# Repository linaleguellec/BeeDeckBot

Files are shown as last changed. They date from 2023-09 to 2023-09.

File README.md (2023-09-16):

# Project presentation 
I completed this project as part of my final year internship as a general engineer specializing in mechanical engineering. 
The aim of the project is to use a single camera to shoot 3D images of bees landing on a moving robotic flower. For more details on the background to this project, please consult my internship report. 

# Folders organization
- beeTracking  : all the algorithms for post-processing the videos (tracing the bee's 3D trajectory from a video in mp4 format). 
- MotorControl : arduino algorithms for motor control.
- robotCAD : the complete digital model of the steel structure in both SolidWorks and STEP formats. 
- technicalDocumentation : all technical documentation (Dynamixel Servomotors, RFID gate ... ). 
- videos : examples of videos taken with the metal structure. The quality of the videos has been reduced to being stored on GitHub.
- results : a summary video of an example of possible results. The quality of the videos has been reduced to being stored on GitHub. 

# Comments  

"MotorControl", "robotCAD", "technicalDocumentation and videos" folders are ready to use. You can use them directly for your projects.

Folders "beeTracking" is not yet powerful enough to be used directly in your projects. I therefore advise you to use them as a first step in your research. 

# Equipment to purchase 
- [a cart](https://www.manutan.fr/fr/maf/table-roulante-noire-2-plateaux-capacite-150-kg-a688743)
- [an RFID door](https://www.microsensys.de/en/solutions/small-animals-identification/)
- [a camera that films at 500 fps](https://www.back-bone.ca/rx0-mod/)
- Please refer to the "invoice" appendix of my internship report for the metallic structure's equipment.

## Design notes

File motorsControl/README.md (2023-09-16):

# Presentation  
This README explains how to set up the electronics to control the motors. In particular, how to start and stop the robotic flower's motors using the manual switch and the RFID door switch. 

# User guide 
Once the metal structure has been assembled, install all the electronic circuits. Transfer the code in this folder to the Arduino UNO board. First, make sure that the electronic circuit without the RFID door is working. Press the manual switch once, the robotic flower target should move with random frequency and amplitude. Press a second time, and the target should stop and move to the position for the next start. 

## Electronics 
Here's the real and theoretical electronic circuit. I've placed the integrated switch of the RFID port and the manual switch in parallel. In this way, the motors of the robotic flower can be controlled either manually by the manual switch, or automatically by the RFID door switch. 
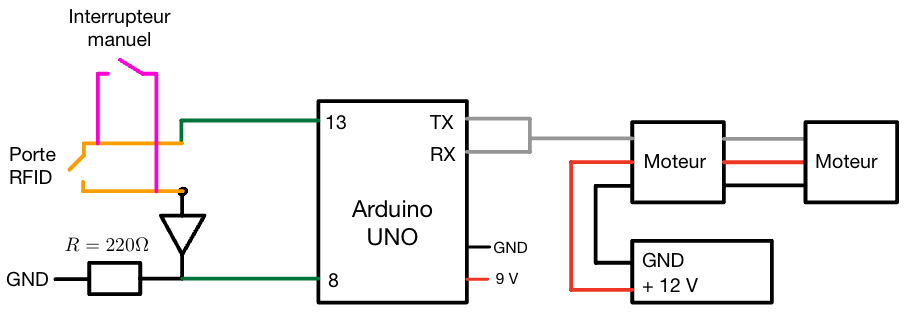
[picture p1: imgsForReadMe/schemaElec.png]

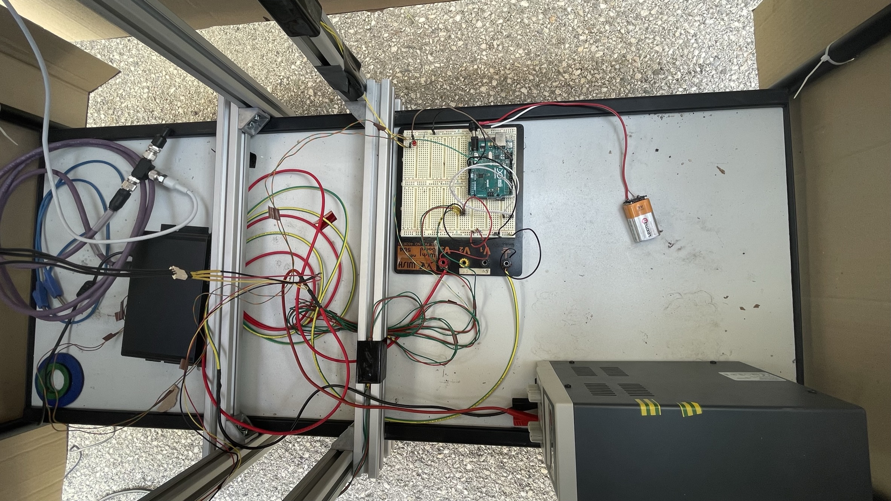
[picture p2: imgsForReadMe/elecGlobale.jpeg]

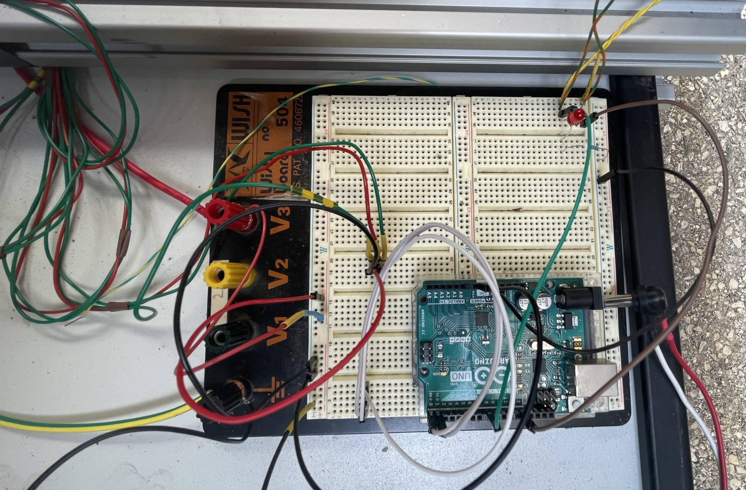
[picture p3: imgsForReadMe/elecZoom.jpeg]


## RFID gate 
- Install the RFID door according to this [technical documentation.](https://github.com/linaleguellec/BeeDeckBot/tree/main/technicalDocumentation/RFIDgate)  

- Attach wires to the back of the RFID door controller as follows. These are the wires for the RFID door's built-in switch. Indeed, as soon as the RFID door detects a bee, the door controller quickly closes its switch. Here's the electronic design from the technical documentation.
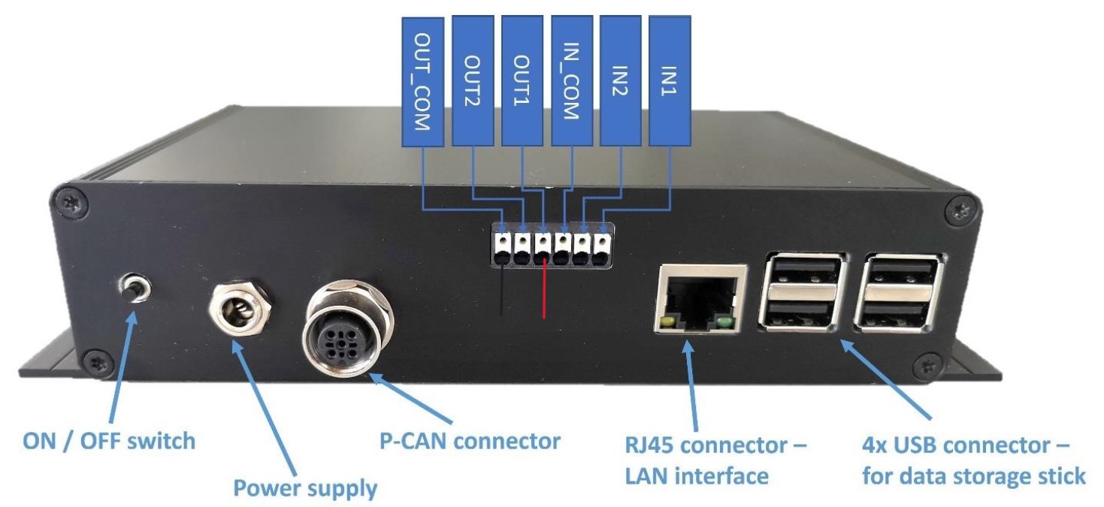
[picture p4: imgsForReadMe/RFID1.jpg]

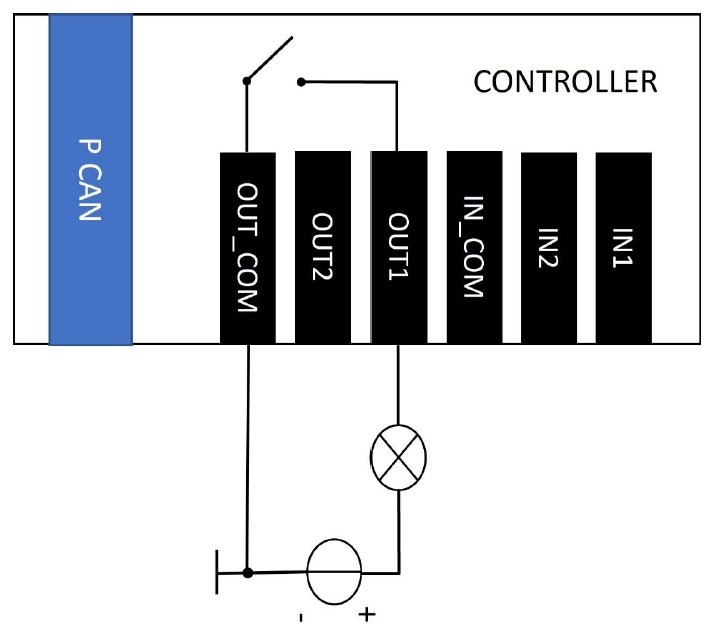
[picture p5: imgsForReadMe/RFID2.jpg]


- For more information about the technical operation of the RFID door, please refer to the ["technical documentation" folder.](https://github.com/linaleguellec/BeeDeckBot/tree/main/technicalDocumentation/RFIDgate)

## Robotic flower control
Please refer to my internship report for an explanation of the robotic flower's motor control algorithm.

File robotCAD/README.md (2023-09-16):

# presentation
In this folder, you'll find all the CAD files for the metallic structure in SolidWorks and Step format. 

# General assembly guide 

- Assemble the flight chamber. 
- Remove the floor from the upper part of the cart.  
- First of all, mount the centre of the metallic part. The part that links the camera, flight chamber, cart and robotic flower.  This part is mounted like a sandwich between the upper rails of the carriage. Adjust its position along the length of the cart so that, once the whole structure is assembled, the 4 wheels of the cart support an equivalent weight. 
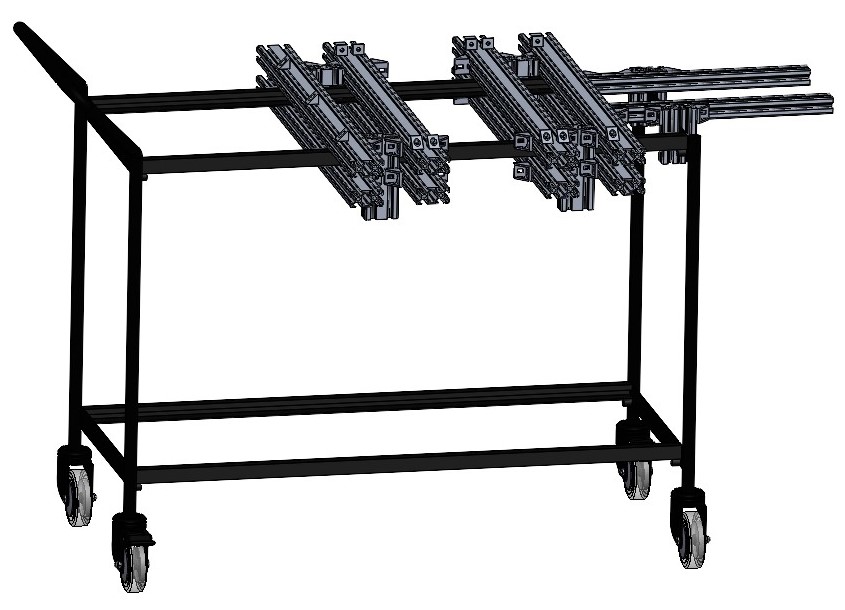
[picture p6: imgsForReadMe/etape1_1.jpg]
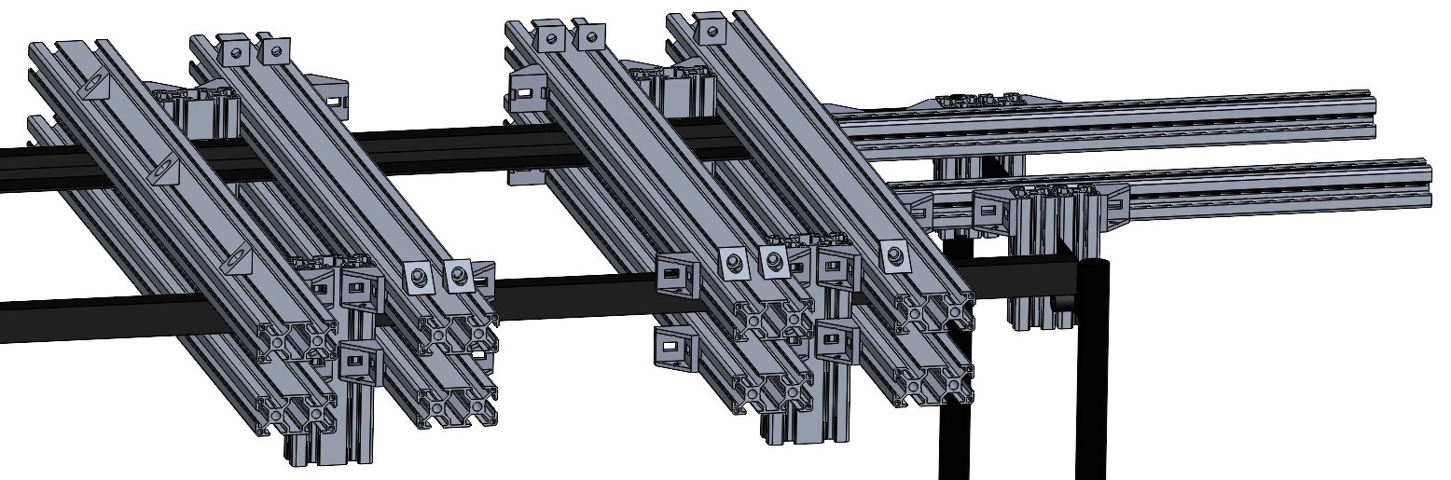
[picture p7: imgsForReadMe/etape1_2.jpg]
 
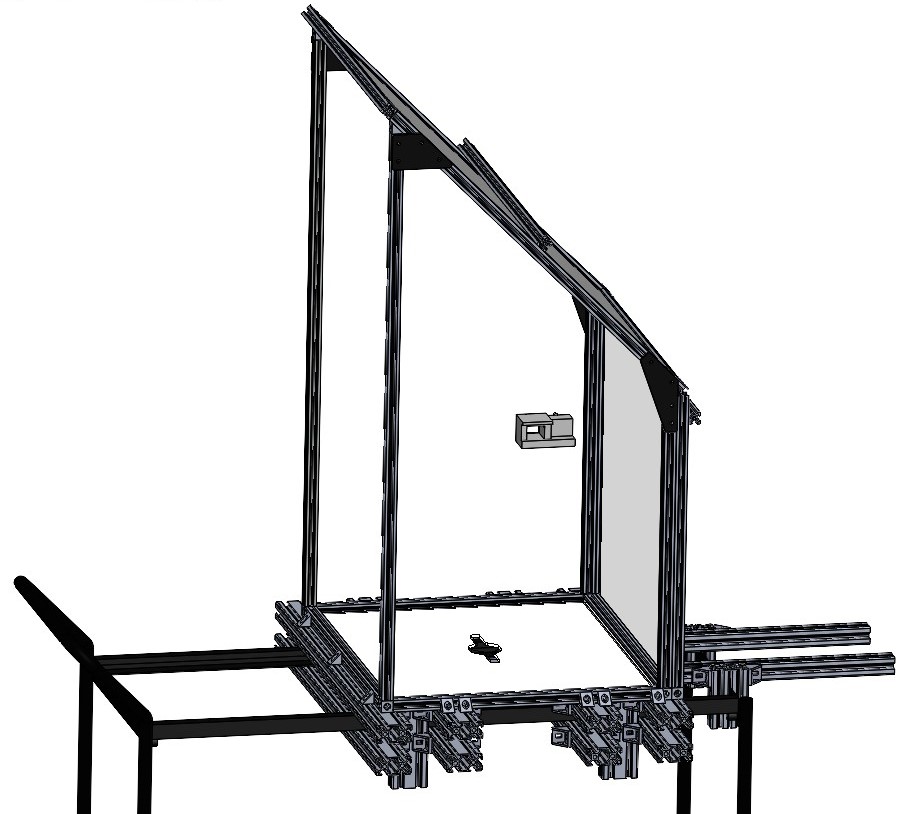
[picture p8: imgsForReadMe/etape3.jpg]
- Attach the flight chamber to the centre of the metal part. 
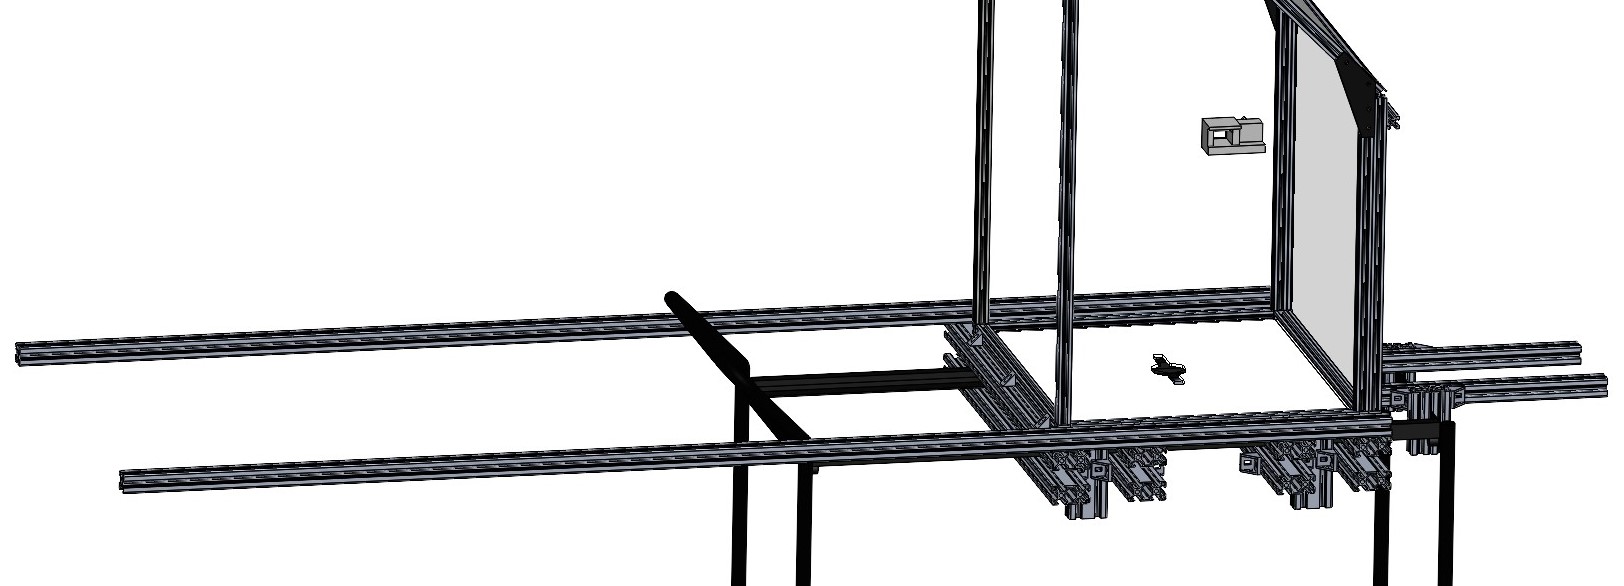
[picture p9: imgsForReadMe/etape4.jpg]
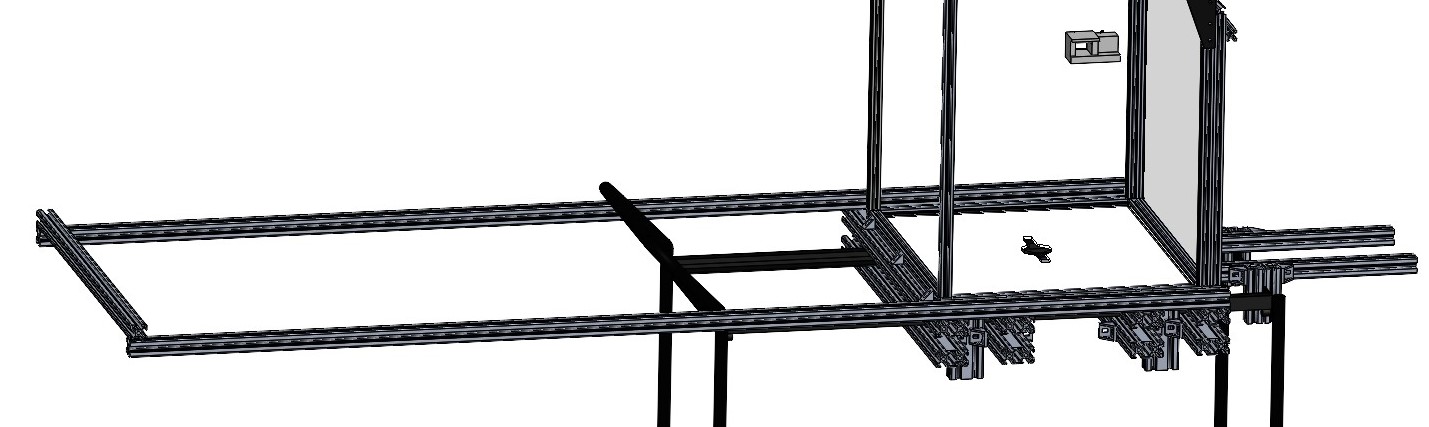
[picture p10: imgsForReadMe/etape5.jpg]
- Install the 2 largest metal bars separating the flight chamber and the camera. Then install the metal bar that makes these 2 largest bars parallel.  
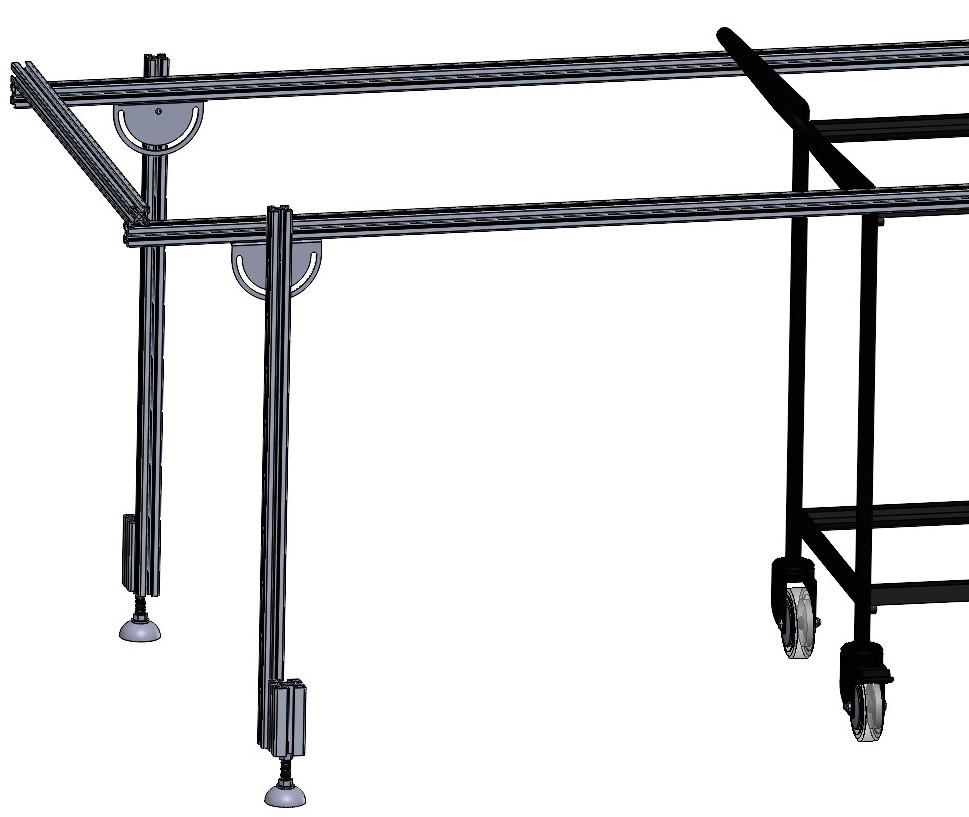
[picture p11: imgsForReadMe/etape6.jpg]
- Fix the folding feet at the ends of the 2 longest bars. Feet support the weight of the camera. 
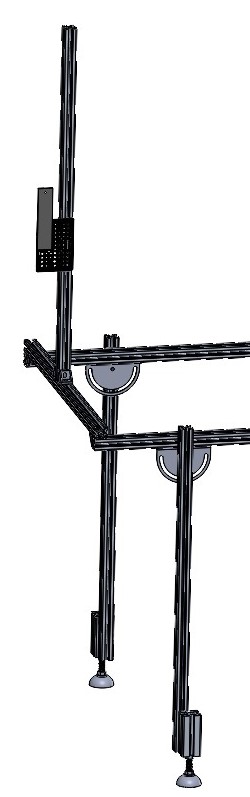
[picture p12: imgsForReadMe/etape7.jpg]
- Attach the camera support. 
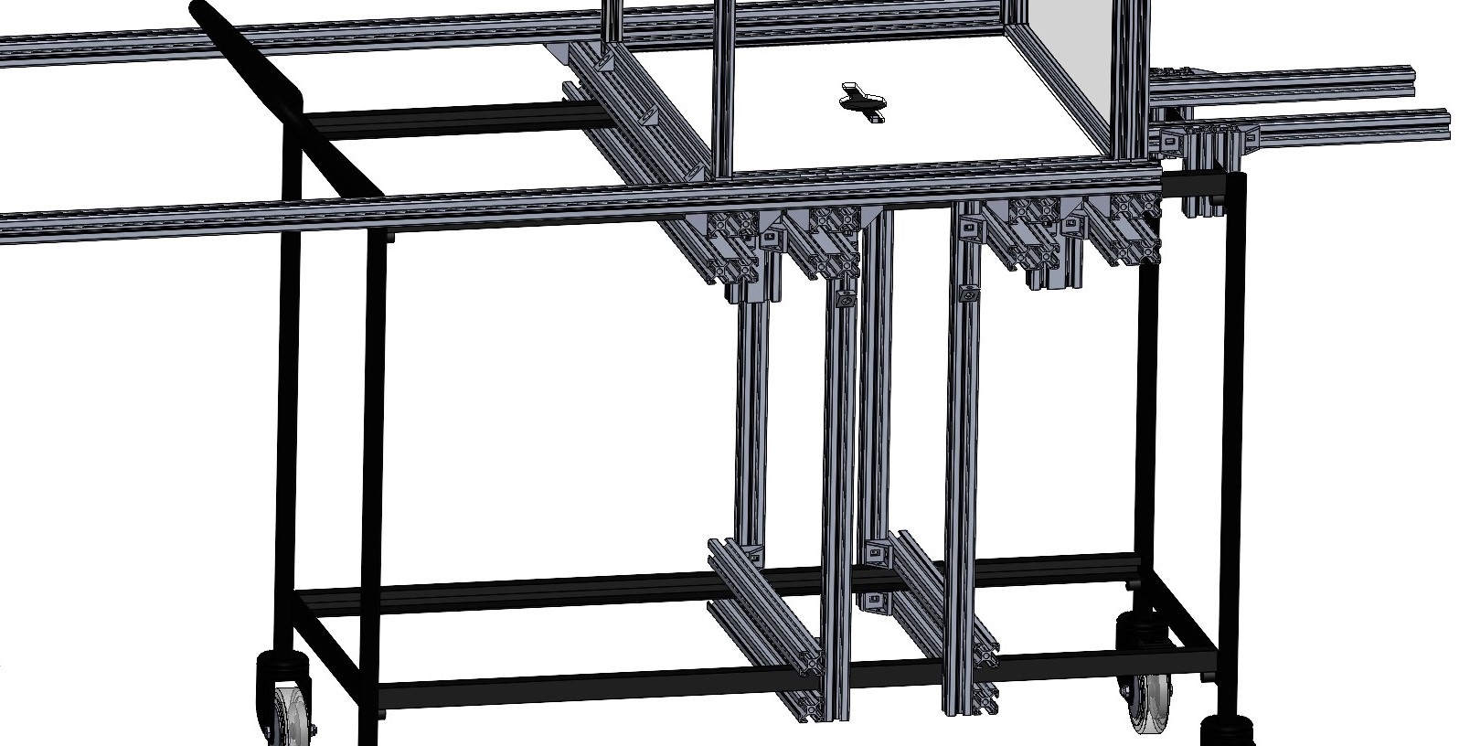
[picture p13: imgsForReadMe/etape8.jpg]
- Attach the metal bars that will support the robotic flower under the flight chamber. 
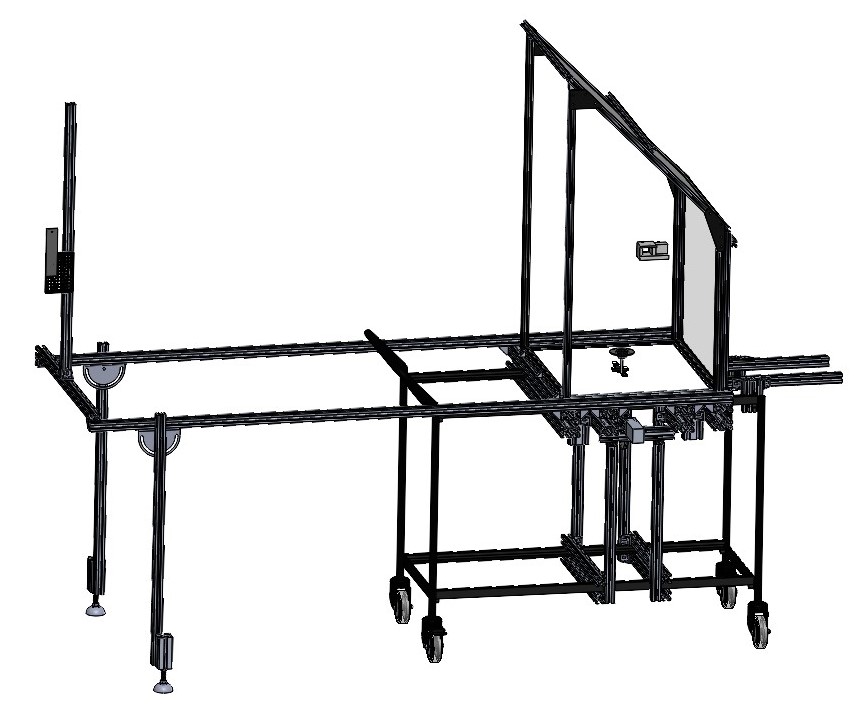
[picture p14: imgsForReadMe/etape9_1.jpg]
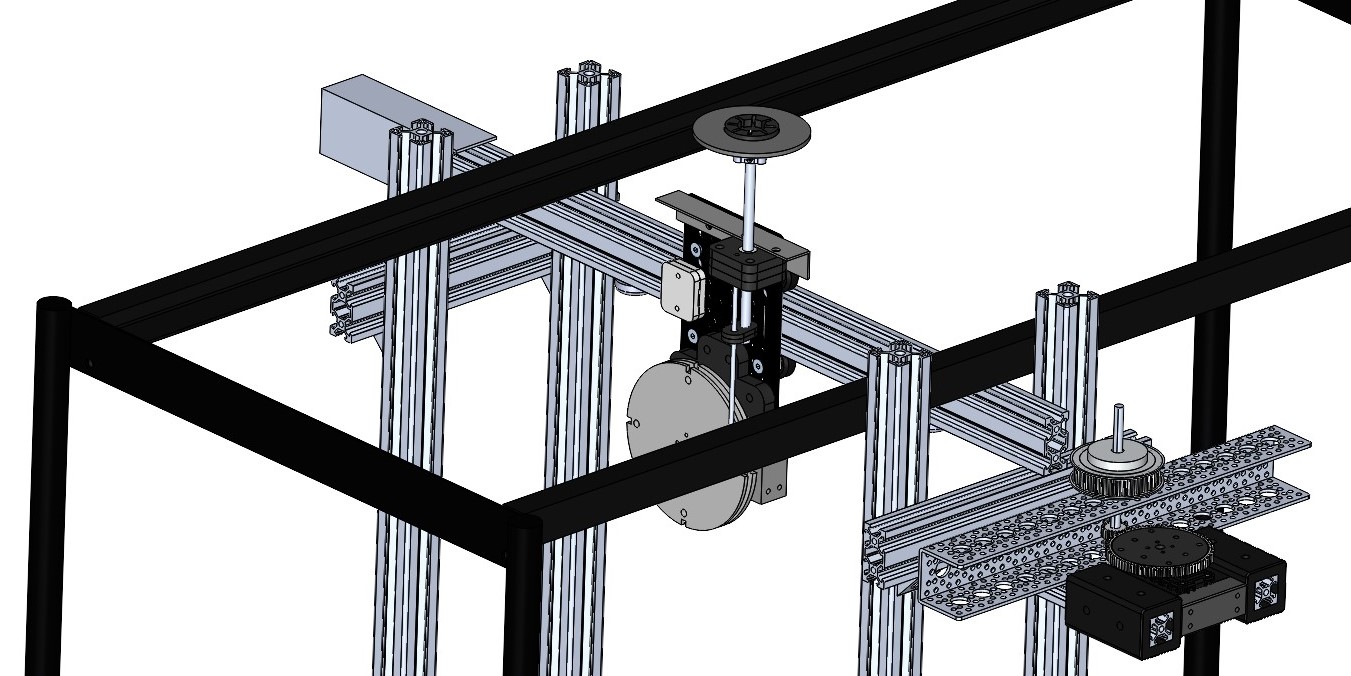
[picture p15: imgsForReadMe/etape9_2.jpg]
- Attach the robotic flower under the flight chamber.   
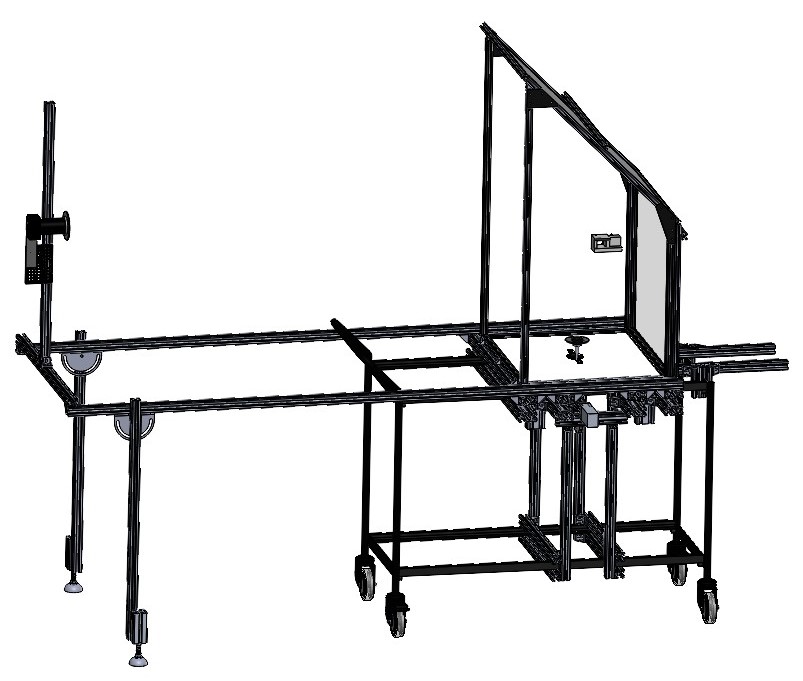
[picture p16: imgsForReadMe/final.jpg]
- Install the camera on the camera holder

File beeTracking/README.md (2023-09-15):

# Presentation 
These files plot the bee's 3D trajectory from a video in mp4 format. 

# Files organization 
- main.py : main file to run 
- tesYOLOv8 : only an algorithm to test the identification method with YOLOv8 instead of my identification method while keeping trajectory tracking with DeepSort. 
- detector.py : contains my own bee detection method.  
- tracker.py : contains a class written by [this developer](https://github.com/computervisioneng/object-tracking-yolov8-deep-sort.git) to make it easier to use DeepSort in the main.py file. 
-deep_sort : contains [this package](https://github.com/computervisiondeveloper/deep_sort) = trajectory tracking algorithms. 
 
# User guide 
- Open the main.py file.
- In the code, specify the path to your bee video in MP4 format. 
- Run code.
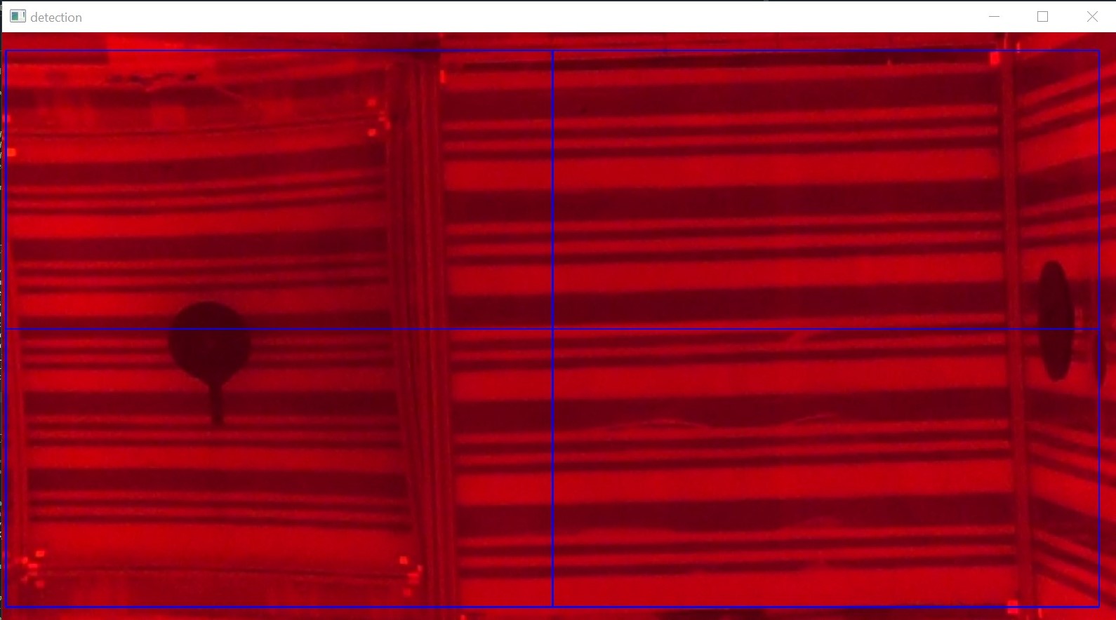
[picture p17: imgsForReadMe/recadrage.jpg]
- A window appears. This is the first frame of your video. Select the area of interest like this example : 
- Press enter when you are sure of your zone selection. 
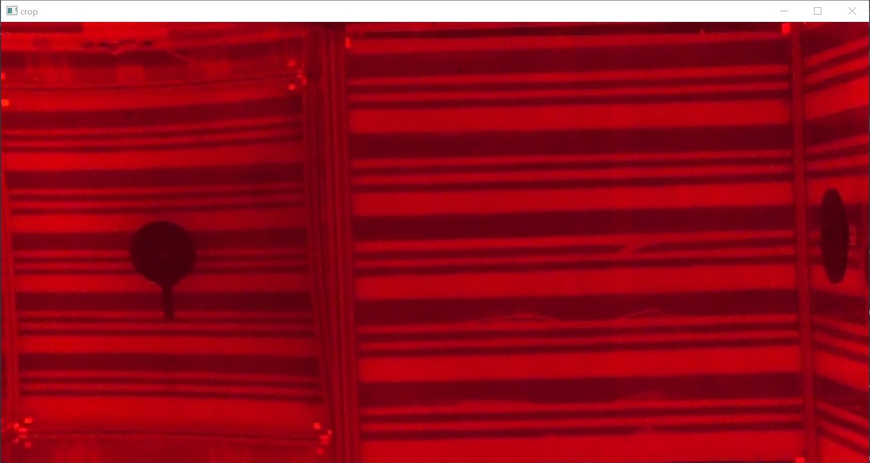
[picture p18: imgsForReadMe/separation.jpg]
- The window will disappear and a second window will be open. It's the first cropped image of your video. 
- Delimit the upper and lower parts of the flight chamber by clicking on the metal bar separating the 2 parts (as shown in this example). The upper part is the image reflected by the mirror.  
- When you are sure of your boundary, press enter.  
- Tracking's calculations will begin. At the end of the calculations, graphics and 3D animation of the bee's trajectory will appear. You can press escape at any time if the calculation time is too long. In this case, the trajectory shown on the final graph will be only a part of the entire trajectory.
- Press p key on the keyboard to pause calculations. Press p again to resume. 
- Set the DEBUG variable to 1 if you want to see the bee identification steps. If not, set DBUG to 0.  

# Sources 
I took inspiration from [this project](https://github.com/computervisioneng/object-tracking-yolov8-deep-sort.git). 

This project tracks objects using YOLOv8 for identification and deepSort for trajectory tracking. 
My project tracks bees using deepSort but not YOLOv8. 
So I took the structure of this project and replaced the YOLOv8 part of my own method of bee identification. 

## Deep Sort
The developer of [this project](https://github.com/computervisioneng/object-tracking-yolov8-deep-sort.git) is working on [this fork](https://github.com/computervisiondeveloper/deep_sort) from deep sort official implementation.

# The main problems with my algorithms 
- The plexiglass mirror is twisted slightly, so the image reflected in the mirror is slightly distorted. My algorithm doesn't correct the distortion caused by the mirror. As so, the bee's trajectory is distorted. 
- Due to the perspective, the image reflected in the mirror is smaller than the image in the lower part of the video (image not reflected in the mirror). The size of the trajectory in the top view is therefore underestimated. 
 - There are still detection errors: as my bee detection algorithm is based on background subtraction, if the camera is not stable and the image vibrates, the background is slightly modified and there are detection errors.  

# How to improve my algorithms ?  

- For the twisted mirror and perspective problem, one way of improving the image is to perform a 3D camera calibration. 3D calibration will correct problems of scale and distortion. 
- To avoid detection errors, one possible improvement is to replace the current bee detection method (background subtraction) with a bee identification method based on artificial intelligence with YOLOv8 and always keeping strongSort.  I tested this method using the YOLOv8 test file. It works well for people detection and tracking.  All we need to do now is to replace YOLOv8's learnt models, adapted to people recognition, with a personalized model adapted to the recognition of our bees.

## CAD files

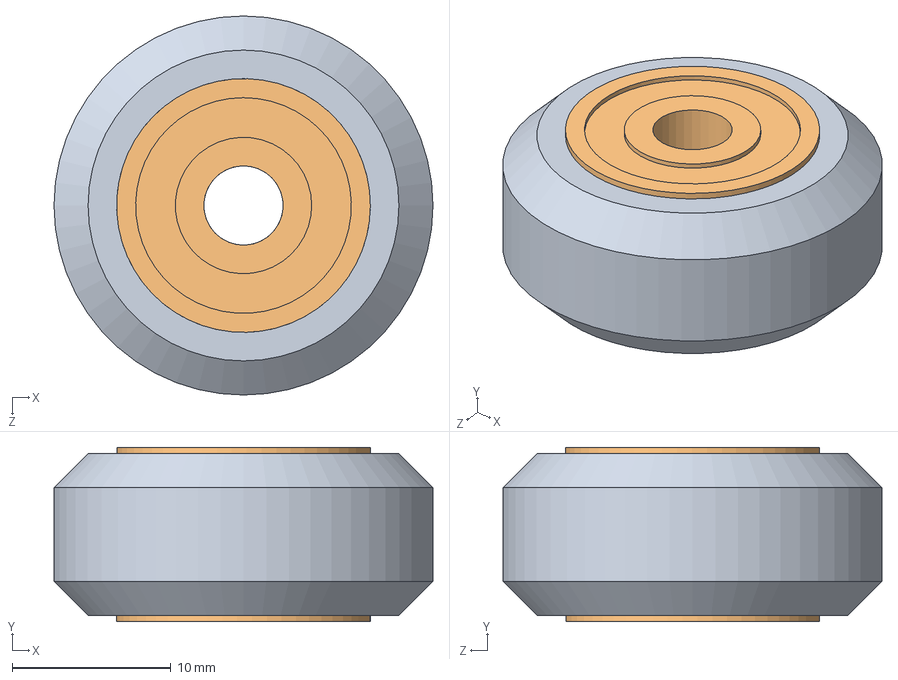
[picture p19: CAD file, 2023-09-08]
robotCAD/Robot_CAD_SoliWorks/User Library-WHL-VSLOT-DLRN.SLDASM
23.9 x 11.0 x 23.9 mm
User Library-WHL-VSLOT-DLRN_Solid V Wheel
User Library-WHL-VSLOT-DLRN_Ball Bearing 5 x 16 x 5 x 2
User Library-WHL-VSLOT-DLRN_Precision Shim 10 x 5 x 1

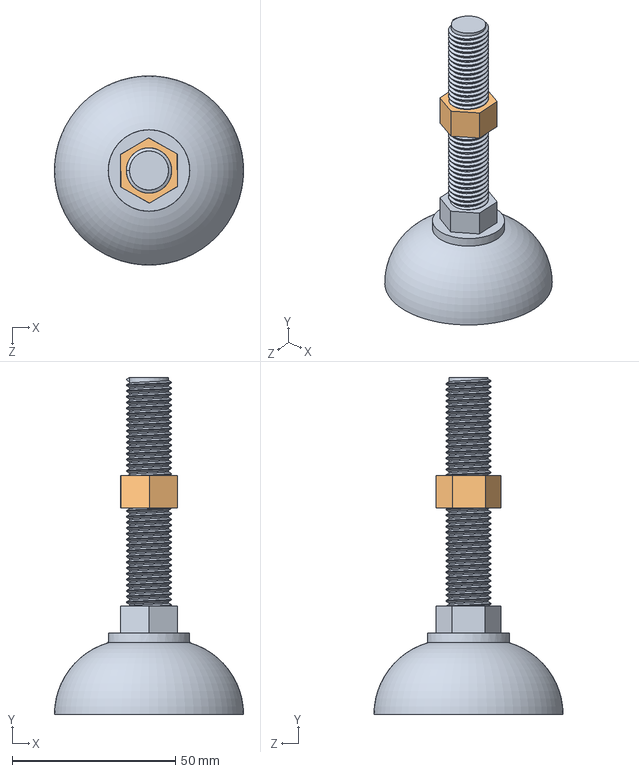
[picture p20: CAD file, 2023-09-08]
robotCAD/Robot_CAD_SoliWorks/User Library-PIED-M12-57.SLDASM
58.0 x 103.3 x 58.0 mm
User Library-PIED-M12-57_PIED-M12-57_1
User Library-PIED-M12-57_PIED-M12-57_2

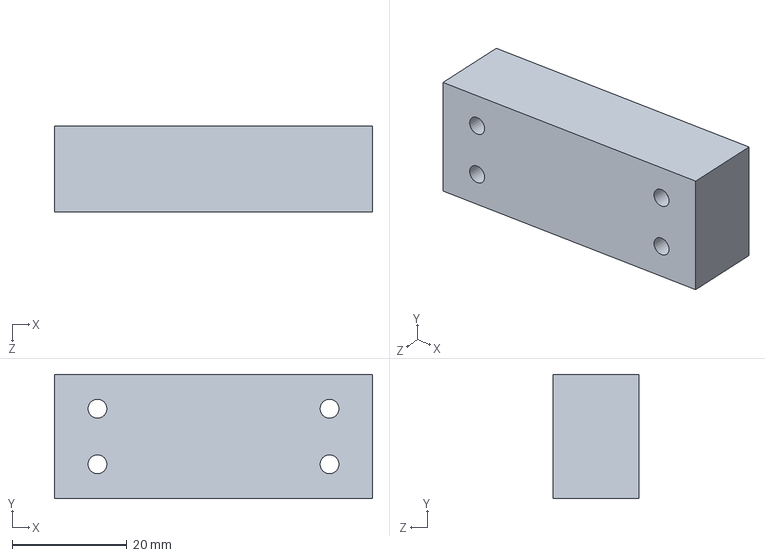
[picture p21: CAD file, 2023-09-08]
robotCAD/Robot_CAD_SoliWorks/fixation moteur 1 refait.SLDPRT
55.5 x 21.7 x 15.0 mm

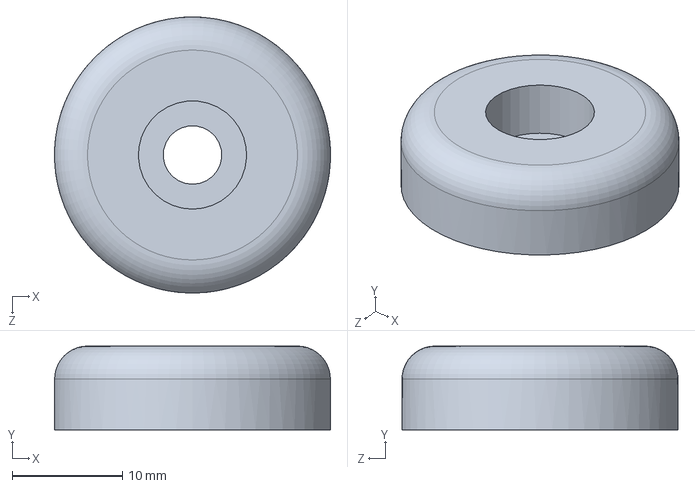
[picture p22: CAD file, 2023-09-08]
robotCAD/Robot_CAD_SoliWorks/User Library-BT-CTC-D25.SLDPRT
25.0 x 7.60 x 25.0 mm

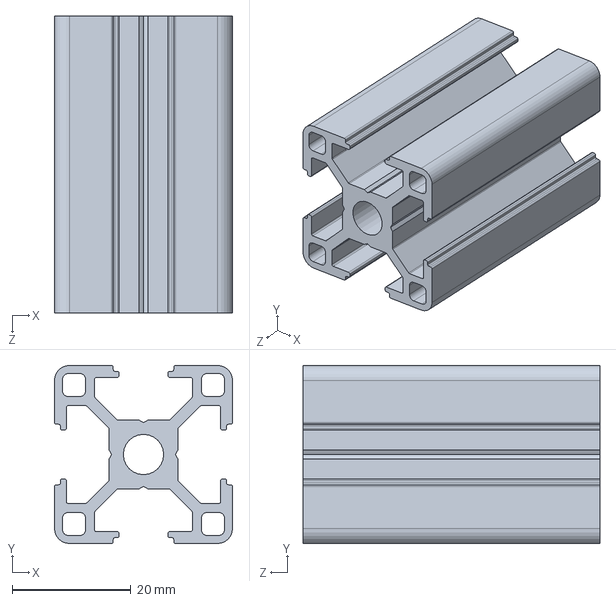
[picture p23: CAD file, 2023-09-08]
robotCAD/Robot_CAD_SoliWorks/piece 6.SLDPRT
30.0 x 30.0 x 50.0 mm

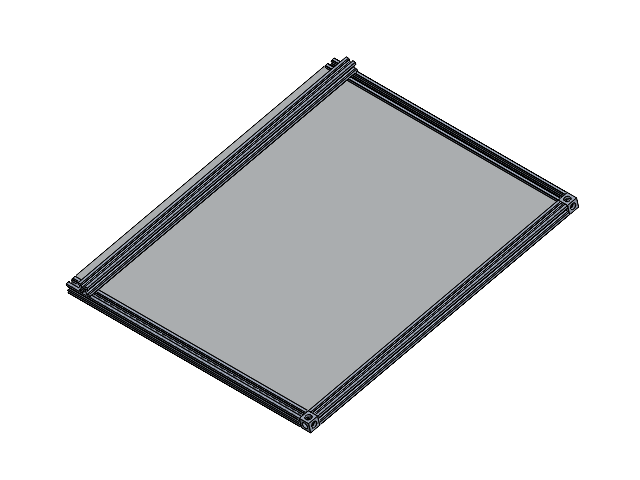
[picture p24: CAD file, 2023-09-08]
robotCAD/Robot_CAD_SoliWorks/Assem_porte_boite_refaite.SLDASM
4-AS-6-2020-VSLOT13
User Library-RACC-CUB-P6-2020-NOIR x 2
4-AS-6-2020-VSLOT14
4-AS-6-2020-VSLOT16
4-AS-6-2020-VSLOT15
arrière

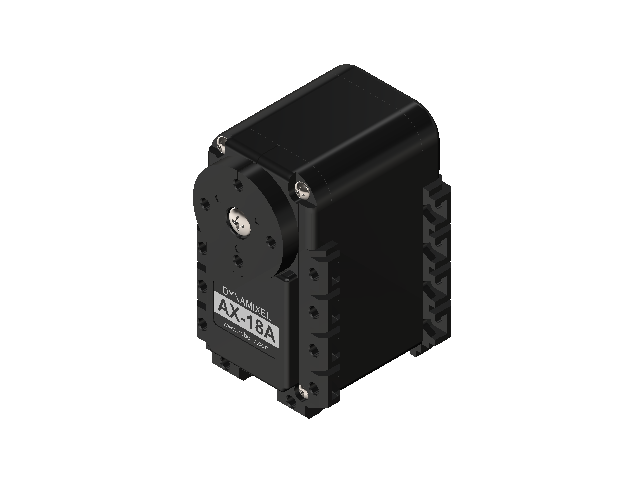
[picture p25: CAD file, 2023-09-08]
robotCAD/Robot_CAD_SoliWorks/AX-18A1.SLDASM
Body^AX-18A1
Wheel Gear^Horn Assembly_AX-18A1
Horn^Horn Assembly_AX-18A1
BHS M2x8^Horn Assembly_AX-18A1
Cover Screws^AX-18A1 x 4
3 Pins Connector^AX-18A1 x 2
Insert M3^AX-18A1

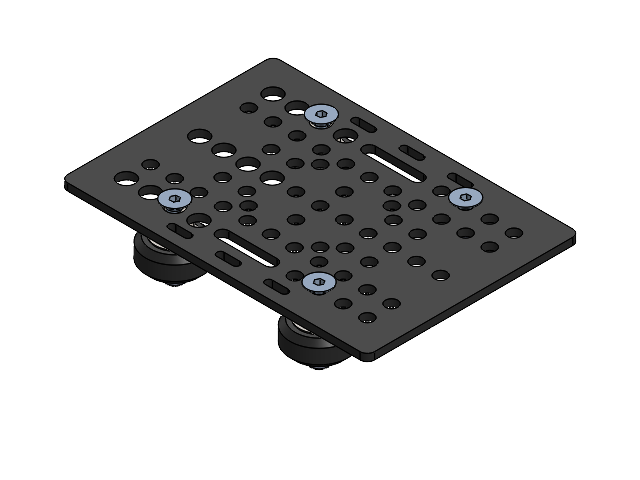
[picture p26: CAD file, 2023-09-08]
robotCAD/Robot_CAD_SoliWorks/plateau_haut.SLDASM
User Library-GANTRY-PLATE-127-88
item_8000118_vis_fhc_m5x30_din_7991_details_3 x 4
User Library-ENTR-EXC-HEX10-6 x 2
entretoise x 2
rondelle x 4
User Library-WHL-VSLOT-DLRN_Solid V Wheel x 4
User Library-WHL-VSLOT-DLRN_Ball Bearing 5 x 16 x 5 x 8
User Library-WHL-VSLOT-DLRN_Precision Shim 10 x 5 x 1 x 4
ecrou_frein2 x 4

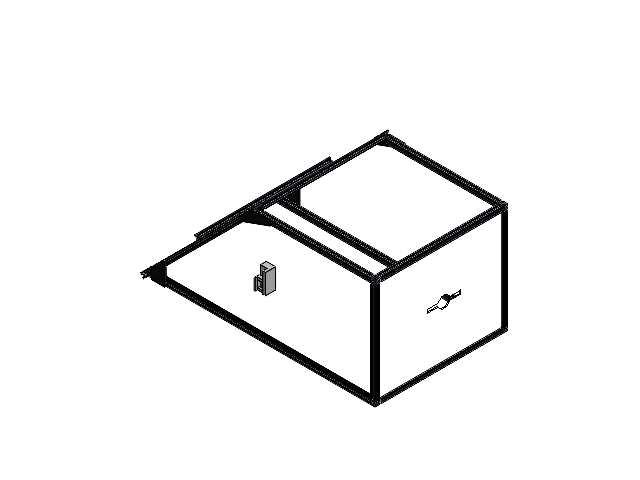
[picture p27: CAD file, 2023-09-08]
robotCAD/Robot_CAD_SoliWorks/Assem_boite_refaite_sans_porte.SLDASM
4-AS-6-2020-VSLOT
User Library-RACC-CUB-P6-2020-NOIR x 4
450-4-AS-6-2020-VSLOT
4-AS-6-2020-VSLOT3
4-AS-6-2020-VSLOT4
4-AS-6-2020-VSLOT5
4-AS-6-2020-VSLOT6
4-AS-6-2020-VSLOT7
4-AS-6-2020-VSLOT8
User Library-EQ-EXT-P6-2020-NOIR x 2
4-AS-6-2020-VSLOT9
4-AS-6-2020-VSLOT10
4-AS-6-2020-VSLOT11 x 2
4-AS-6-2020-VSLOT12
renfort côté bas x 2
renfort côté haut dr
renfort côté haut ga
base_boite
panneau gauche ouverture
miroir
avant
panneau droit
porte RFID
User Library-ML-ANG-90 x 4

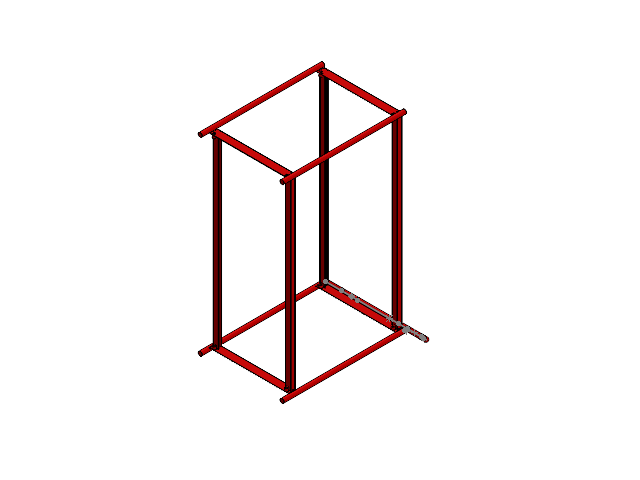
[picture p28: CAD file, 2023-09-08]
robotCAD/Robot_CAD_SoliWorks/chario.SLDASM
grand_cote
fente x 4
petit_cote

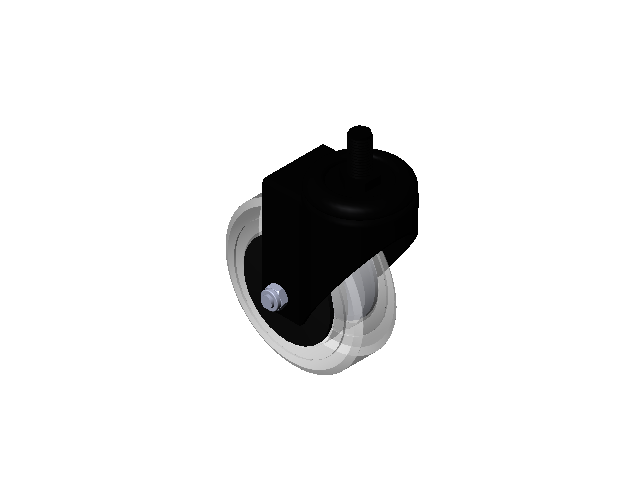
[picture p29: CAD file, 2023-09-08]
robotCAD/Robot_CAD_SoliWorks/4prh5112a.SLDASM
4prh5112a_01
4prh5112a_02
4prh5112a_03
4prh5112a_04
4prh5112a_05
4prh5112a_06
4prh5112a_07

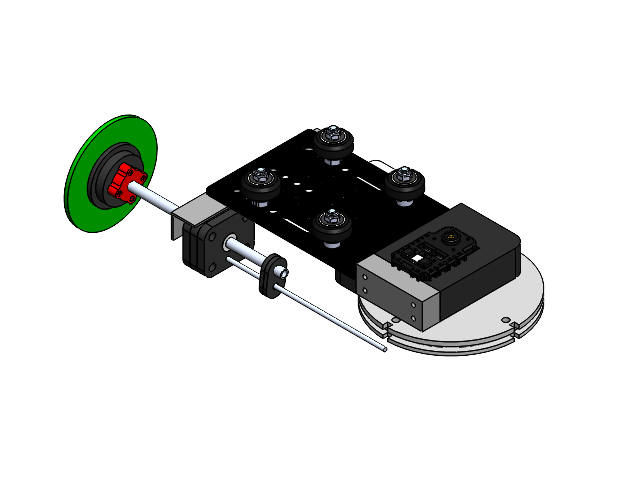
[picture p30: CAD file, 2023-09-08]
robotCAD/Robot_CAD_SoliWorks/partie_haute.SLDASM
fixation moteur 1 refait
fixation moteur 2 refait
Body^AX-18A
Wheel Gear^Horn Assembly_AX-18A
Horn^Horn Assembly_AX-18A
BHS M2x8^Horn Assembly_AX-18A
Cover Screws^AX-18A x 4
3 Pins Connector^AX-18A x 2
Insert M3^AX-18A
User Library-GANTRY-PLATE-127-88
item_8000118_vis_fhc_m5x30_din_7991_details_3 x 4
User Library-ENTR-EXC-HEX10-6 x 2
entretoise x 2
rondelle x 4
User Library-WHL-VSLOT-DLRN_Solid V Wheel x 4
User Library-WHL-VSLOT-DLRN_Ball Bearing 5 x 16 x 5 x 8
User Library-WHL-VSLOT-DLRN_Precision Shim 10 x 5 x 1 x 4
ecrou_frein2 x 4
roue haut
equ_fix_fleur
fix_roulement_fleur x 3
axe_fleur
roul_fleur
fleur
545576_1.STEP
632138_91375A438_1.STEP
fleur50
crante
lisse
connecteur axe fleur x 2
petit axe fleur

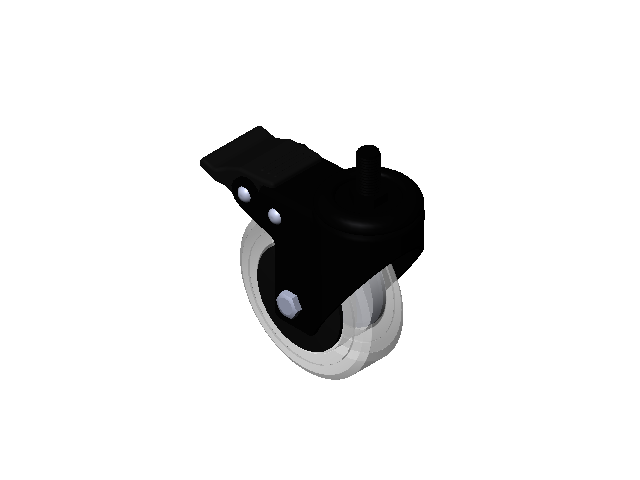
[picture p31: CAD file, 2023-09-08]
robotCAD/Robot_CAD_SoliWorks/4prh5112b.SLDASM
4prh5112b_01
4prh5112b_02
4prh5112b_03
4prh5112b_04
4prh5112b_05
4prh5112b_06
4prh5112b_07
4prh5112b_08
4prh5112b_09
4prh5112b_10

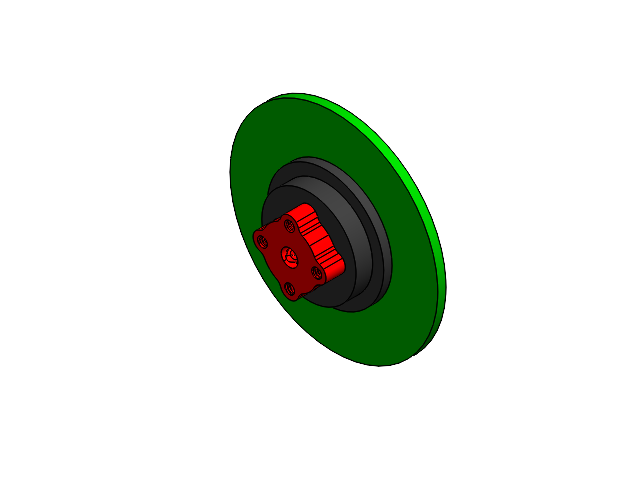
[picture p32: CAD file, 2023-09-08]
robotCAD/Robot_CAD_SoliWorks/fleur_assemble.SLDASM
fleur
545576_1.STEP
632138_91375A438_1.STEP
fleur50

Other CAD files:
robotCAD/Robot_CAD_SoliWorks/AX-18A.SLDASM
robotCAD/Robot_CAD_SoliWorks/Assem1.SLDASM
robotCAD/Robot_CAD_SoliWorks/renfort côté haut ga.SLDPRT
robotCAD/Robot_CAD_SoliWorks/miroir.SLDPRT
robotCAD/Robot_CAD_SoliWorks/1-6-AS-6-2040-VSLOT.SLDPRT
robotCAD/Robot_CAD_SoliWorks/2-6-AS-6-2040-VSLOT.SLDPRT
robotCAD/Robot_CAD_SoliWorks/4-AS-6-2020-VSLOT.SLDPRT
robotCAD/Robot_CAD_SoliWorks/4-AS-6-2020-VSLOT10.SLDPRT
robotCAD/Robot_CAD_SoliWorks/4-AS-6-2020-VSLOT11.SLDPRT
robotCAD/Robot_CAD_SoliWorks/4-AS-6-2020-VSLOT12.SLDPRT
robotCAD/Robot_CAD_SoliWorks/4-AS-6-2020-VSLOT13.SLDPRT
robotCAD/Robot_CAD_SoliWorks/4-AS-6-2020-VSLOT14.SLDPRT
robotCAD/Robot_CAD_SoliWorks/4-AS-6-2020-VSLOT15.SLDPRT
robotCAD/Robot_CAD_SoliWorks/4-AS-6-2020-VSLOT16.SLDPRT
robotCAD/Robot_CAD_SoliWorks/4-AS-6-2020-VSLOT3.SLDPRT
robotCAD/Robot_CAD_SoliWorks/4-AS-6-2020-VSLOT4.SLDPRT
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

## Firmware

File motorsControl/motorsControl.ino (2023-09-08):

/*
 * author : Lina Le Guellec
 * date : 08/09/2023
 * This code sets the 2 axes of the robotic flower in motion. 
 * The robotic flower imitates the movement of a flower.
 * The frequencies, amplitudes and phase of the horizontal and vertical axes are chosen randomly each time the switch is triggered.
 */



#include <Arduino.h>
#include "DynamixelMotor.h"
#include <MatrixMath.h>
     
#define pi    3.1415926535897932384626433832795

long t_0, t_1, t;

int angle[2] = {1023/2, 1023/2};
int init_angle[2];

float r[2] = {5, 12.14};

float Ax_tab[] = {3.0, 5.0, 7.0};
float Az_tab[] = {1.0, 2.0, 3.0};
float fx_tab[] = {0.2, 0.3, 0.5};
float tau_tab[] = {0.0, 0.25, 0.5, 0.75, 1.0};

float f_z, f_x, A_z, A_x, phi_x, phi_z;
float tau;


const uint8_t id_z =1;
const uint8_t id_x =2;

int16_t spe=1023;
const long unsigned int baudrate = 1000000;

HardwareDynamixelInterface interface(Serial);

DynamixelMotor motor_z(interface, id_z);
DynamixelMotor motor_x(interface, id_x);

int etat = 0;
int trig = 0;
int trig_pin = 5;

int rfid_pin = 8;
int rfid_pin_val = 0; 
int rfid_pin_val_was = 0;

/*
XXXXXXXXXXXXXXXXXXXXXXXXXXXXXXXXXXXXXXXXXXXXXXXXXXXXXXXXXXXXXXXXXXXXXXXXXXXXXXXXXXXXXXXXXXXXXXXXXXXXXXXXXXXXXXXXXXXXXXXXXXXXXXXXXXXXXXXXXXXXXXXXXXXXXXXXXXXXXXXXXXXXXXXXXXXXXXXXXXXXXXXXXXXXXXXXXXXXXXXXXXXXXXXXXXXXXXXXXXXXXXXXXXXXXXXXX
*/
void setup()
{ 
  pinMode(trig_pin, INPUT);
  pinMode(6, OUTPUT);
  digitalWrite(6, HIGH);
  /*++++++++++++++++++++++++++++++++++++++++++++++++++*/
  pinMode(rfid_pin, INPUT);
  pinMode(13, OUTPUT);
  digitalWrite(13, HIGH);
  /*++++++++++++++++++++++++++++++++++++++++++++++++++*/
  interface.begin(baudrate);
  delay(100);
  uint8_t status_x=motor_x.init();
  if(status_x!=DYN_STATUS_OK)
  {
    pinMode(LED_BUILTIN, OUTPUT);
    digitalWrite(LED_BUILTIN, HIGH);
    while(1);
  }
  motor_z.enableTorque();  
  motor_z.jointMode(0, 1023);
  motor_z.speed(spe);
  
  motor_x.enableTorque();  
  motor_x.jointMode(0, 1023);
  motor_x.speed(spe);

  delay(200);
  init_phase();

  delay(1000);
  
  /*++++++++++++++++++++++++++++++++++++++++++++++++++*/
  t_0 = millis();
  /*++++++++++++++++++++++++++++++++++++++++++++++++++*/
 
}

/*
XXXXXXXXXXXXXXXXXXXXXXXXXXXXXXXXXXXXXXXXXXXXXXXXXXXXXXXXXXXXXXXXXXXXXXXXXXXXXXXXXXXXXXXXXXXXXXXXXXXXXXXXXXXXXXXXXXXXXXXXXXXXXXXXXXXXXXXXXXXXXXXXXXXXXXXXXXXXXXXXXXXXXXXXXXXXXXXXXXXXXXXXXXXXXXXXXXXXXXXXXXXXXXXXXXXXXXXXXXXXXXXXXXXXXXXXX
*/

 void init_phase(){

    int taille_Ax_tab = sizeof(Ax_tab)/sizeof(Ax_tab[0]);
    int taille_Az_tab = sizeof(Az_tab)/sizeof(Az_tab[0]);
    int taille_tau_tab = sizeof(tau_tab)/sizeof(tau_tab[0]);
    int taille_fx_tab = sizeof(fx_tab)/sizeof(fx_tab[0]);
  
    int index_Ax_tab = random(taille_Ax_tab);
    int index_Az_tab = random(taille_Az_tab);
    int index_tau_tab = random(taille_tau_tab);
    int index_fx_tab = random(taille_fx_tab);
    
    A_x = Ax_tab[index_Ax_tab];
    A_z = Az_tab[index_Az_tab];
    tau = tau_tab[index_tau_tab];
    f_x = fx_tab[index_fx_tab];

    f_z = 2*f_x;

    if ( tau < 0.25) {
      phi_x = (pi/2)*(1 - 4*tau);
      phi_z = (pi/2)*(8*tau - 1);
    }
  
    else if ( tau < 0.5) {
      phi_x = (pi/2)*(1 - 4*tau);
      phi_z = - (pi/2)*(8*(tau - 0.25) - 1);
    }
    
    else if ( tau < 0.75) {
      phi_x = - (pi/2)*(1 - 4*(tau - 0.5));
      phi_z = (pi/2)*(8*(tau - 0.5) - 1);
    }
    
    else {
      phi_x = - (pi/2)*(1 - 4*(tau - 0.5));
      phi_z = - (pi/2)*(8*(tau - 0.75) - 1);
    }
 
}
  


void Gestion(){
  
  rfid_pin_val_was = rfid_pin_val;
  rfid_pin_val = digitalRead(rfid_pin);
  
  switch(etat){

    case 0:
      if (rfid_pin_val == 1 and  rfid_pin_val_was == 0){
        etat = 1;
        delay(500);
        t_0 = millis();
      }
    break;
    
    case 1:
      if (rfid_pin_val == 1 and  rfid_pin_val_was == 0){
        etat = 0;
        init_phase();
        Serial.print("init phase");
        delay(500);
      }
    break;
    
  }
}

void Action(int etat){
   switch(etat){
    case 0:
      init_mov();
      motor_z.goalPosition(init_angle[0]);
      motor_x.goalPosition(init_angle[1]);
    break;

    case 1:
      gen_mov();
      motor_z.goalPosition(angle[0]);
      motor_x.goalPosition(angle[1]);
    break;
  }

  
}


void gen_mov(){
  
  float z_d =  sin((2.00*pi*f_z*(float)t/1000) + phi_z);
  z_d = 0.5*(z_d-1.00)*A_z;

  float x_d =  sin(2.00*pi*f_x*(float)t/1000 + phi_x);
  x_d = 0.5*(x_d)*A_x;

  float a_z = atan((z_d/r[0]))*(180/pi);
  float a_x = atan((x_d/r[1]))*(180/pi);
  
  angle[0] = (int)((1023/2) + (a_z*1023/300));
  angle[1] = (int)((1023/2) + (a_x*1023/300));
  
}

void init_mov(){
  
  float z_d =  sin(phi_z);
  z_d = 0.5*(z_d-1.00)*A_z;

  float x_d =  sin(phi_x);
  x_d = 0.5*(x_d)*A_x;

  float a_z = atan((z_d/r[0]))*(180/pi);
  float a_x = atan((x_d/r[1]))*(180/pi);
  
  init_angle[0] = (int)((1023/2) + (a_z*1023/300));
  init_angle[1] = (int)((1023/2) + (a_x*1023/300));
  
}

/*
XXXXXXXXXXXXXXXXXXXXXXXXXXXXXXXXXXXXXXXXXXXXXXXXXXXXXXXXXXXXXXXXXXXXXXXXXXXXXXXXXXXXXXXXXXXXXXXXXXXXXXXXXXXXXXXXXXXXXXXXXXXXXXXXXXXXXXXXXXXXXXXXXXXXXXXXXXXXXXXXXXXXXXXXXXXXXXXXXXXXXXXXXXXXXXXXXXXXXXXXXXXXXXXXXXXXXXXXXXXXXXXXXXXXXXXXX
*/

void loop() 
{
  t_1 = millis();
  t = (t_1-t_0); 
  Gestion();
  Action(etat);

}

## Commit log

2023-07-20 Create moteurs_v3.ino
    code arduino
2023-07-20 camera calibration
2023-09-12 animation 3D
    [fleur.obj]
